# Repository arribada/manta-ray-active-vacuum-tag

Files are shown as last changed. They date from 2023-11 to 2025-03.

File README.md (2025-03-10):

# Oceanic Manta Ray Active Vacuum Tag

manta_tag

## About

This repository details ongoing research and development work by [Arribada](https://arribada.org) to develop an active vacuum (suction) cup tag, primarily to provide a non-invasive means of attaching scientific instruments to oceanic manta rays i.e accelerometers, video cameras or other instruments to advance scientific research conducted by the [Bureau of Ocean Energy Management](https://www.boem.gov/) in partnership with [Georgia Aquarium](https://www.georgiaaquarium.org/).

### Active vacuum cup "tadpole" design

manta_vacuum_tag_github

## Purpose

The oceanic manta ray active vacuum tag was developed to provide a non-invasive means of attaching bio-logging instruments to oceanic manta rays by means of utilising a vacuum cup and active suction to attach bio-logging payloads to the manta's skin. It is primarily intended for attachment in-water by scuba divers, although a pole-based attachment mechanism is under development. Typical use cases involve attaching GPS/GNSS positioning instruments, accelerometers and other bio-logging apparatus.

The tag has been designed to fit Arribada's open source [Horizon ARTIC R2 Argos satellite / GNSS transmitter](https://arribada.org/horizon-gps-tracking/) to provide satellite positioning for recovery when on the surface. Other payloads, such as accelerometers, of optional VHF pingers can be fitted to either side of the tag's cylindrical mounting holes.

The design files in this repository contain all of the components and necessary to build the physical tag. You are free to select your own electronics / payloads, or to use the Horizon transmitter which fits the tag natively.

## Design

To get started with the design, head to the [hardware](https://github.com/arribada/manta-ray-active-vacuum-tag/tree/main/Hardware) directory.
Here you will find the assembly instructions and design files for the tag.

## Changelog

### v1.02a - 2024-07-15

- Documentation clean up for public release

### v1.02 - 2024-06-01

- Initial release and publish to OSHWA

## Licence

All hardware designs, files, assets and schematics in this repository are licenced under CERN OHL v1.2. Documentation is licenced under GPLv3.
The design files are certified open source hardware by the Open Source Hardware Association, certification UID [UK000063](https://certification.oshwa.org/uk000063.html).

CERN OHL v1.2

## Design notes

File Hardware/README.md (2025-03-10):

# Hardware Design

The design specification of the payload was to primarily generate a vacuum underwater, removing water and air trapped within a vacuum cup when applied to the surface of a target animal quickly and efficiently. To achieve this, the payload itself needed to be slightly positively buoyant to aid recovery after being a) mechanically vented through the use of a corrodible plug to fill the vacuum with water and thus detach, or b) retained in place via a watertight / airtight seal until otherwise vented via a mechanical process.

Once on the surface, the tail of the tag should point towards the sky as it is the lightest part of the instrument. The base remains in the water carrying the payloads, exposing the whip antenna in the tail and allowing recovery by VHF (pinger) or Argos telemetry using an embedded [Arribada Horizon satellite transmitter](https://arribada.org/product/arribada-horizon-artic-r2-developers-kit/).

Early iterations of the design utilised a modified commerical vacuum cup insert, with an attempt to reduce total weight made by milling away surface metal of the internal disk. Ultimately the overall weight and need to include additional syntactic foam to increase buoyancy required a custom ABS insert to be CNC milled instead, replacing the metal off-the-shelf variant. An example of a typical commercial vacuum cup insert with vacuum socket has been provided below. Typically, the weight of a vacuum cup insert is not a defining factor if used in a vacuum assembly line, however in our case the weight needed to be reduced significantly.



## Manufacturing

## Version v1.02

We recommend that you inspect the [bill of materials (BOM)](./bom/manta_active_vaccum_tag_bom.xlsx) necessary to build the tag, inspect the 3D printable assets, the CNC millable assets, and all of the necessary components required to develop and test the tag before proceeding.

The tag consists of a 3D printable payload holder, typically printed in nylon (PA 11), attached to an ABS vacuum insert that are both printable and millable on suitable desktop 3D printers and mills (i.e. the Bambu X1 that supports nylon and the Carvera Desktop CNC). If you don't have access to suitable 3D printers or CNC machines the files can readily be printed and milled by third parties.

All other required components, such as the vacuum cup, air hose, venturi vacuum generator and Prevost quick attachment adapter are noted in the BOM and can be purchased from multiple online retailers.

### 1. Preparing the custom vacuum cup insert

The tag was designed to attach to and support the use of a Fipa ref.102.160.380.4 vacuum cup, a 160mm diameter cup originally designed to lift rough materials (sawn wood or materials with rough or uneven surfaces). Fipa cups can be purchased from any Fipa authorised supplier. We purchased our cups from Hennig UK Ltd, who selected the cup based on our requirements - size, grip and suitability for us to redesign a lighter open source vacuum insert to replace the metal insert that is typically used with standard vacuum machinery.

To reduce the overall weight of the tag and to increase buoyancy it was necessary to develop a custom ABS vacuum cup insert, filled with pre-cut syntactic foam, thus essentially creating a positively buoyant vacuum insert to replace the metal commerical off-the-shelf variant (described above) that was too heavy to utilise. Our re-designed insert fits the Fipa ref.102.160.380.4 vacuum cup and can be CNC milled in ABS using the supplied STEP files in the [/hardware](./cad/) directory of this repository.



When milling with a suitable CNC machine, the external (top) face of the insert needs to be milled flush (+/- 0.1mm tolerance) with a step on the lip to fit the FiPA vacuum cup (see below). In the graphic below the venting hole can be seen next to the central air extraction hole. A 1/4 BSPP non-return valve (RS PRO Non Return Valve, 10mm Tube Outlet - 144-2704) is attached after tapping the hole with a 1/4 tapping tool. Use plumbing tape (PTFE Tape) on the threads to ensure a watertight seal and secure with a 1/4 BSPP locking nut on the internal side (RS PRO Stainless Steel Locknut, 1/4 BSPP - 762-1184).



Alignment rings should be greased in a synthetic lubricant to help guide the nitrile rubber vacuum cup into position. Note - use a good amount of synthetic lubricant, such as super lube multi-purpose synthetic grease on the centre hole to help push the nitrile rubber inner ring into place. Without grease it can be quite challenging, but with grease it's possible to ease it in slowly, working your way around in a circle until the entire inner ring is flush with the ABS disk.



The FiPA nitrile rubber vacuum cup we selected is designed for stacking partially air-permeable plate materials, so we selected it to help work with the manta's slime layer that we would ultimately need to attach to. We also selected this type of cup as it has a soft sealing lip made of abrasion-resistant nitrile and has a large surface area, although we intend to replace this part for a ClingTech variant in the near future (testing is still underway) that may enhance attachment further.



### 2. Preparing the multi-jet fusion 3D printed body

The body of the tag is constructed in two halves (all STEP files are available in the hardware folder of this repo). The material used is PA 12, using either selective laser sintering (SLS) or multi-jet fusion 3D printing processes to form the body. PA 12 is porous, but as we are attaching payloads separately we don't need to worry about water ingress - instead the body forms a hydrodynamic structure in which to hold the payloads, syntactic foam and push water over the air hose coupler in the centre to minimise drag.

The image below details the assembly of the body. Accu stainless steel M4 socket flanger screws (50mm and 30mm) are used to attach the 3D printed body to the CNC milled ABS vacuum cup insert / base. Foam is cut and place in the internal cavity. Based on your choice of payload (weight), the foam can be removed or topped up as necessary to balance the tag and provide a slight amount of positive buoyancy. Mounting holes on the ABS insert are drilled to M3 in size ready to be tapped to M4 using a tapping tool. Once tapped you should drill the mounting holes out slightly in the 3D printed SLS leaving a little bite so there is additional grip still and the hole is tight to accept the screw and secure the body in place.



A complete bill of materials is available [here](./bom/manta_active_vaccum_tag_bom.xlsx) to reconstruct the tag. It should be possible to replicate the tag with access to a 3D printer, 3-axis CNC machine and a basic workbench to aid tapping the threads and installing the air hose coupler.

It's important to use a stainless steel Prevost coupler vs the standard variant as the ball-bearings inside the coupler are brass vs stainless steel and will rust over time when exposed to salt water. The image below shows a Prevost coupler attached to the tag. The green button can be pressed with a single hand when in the water to detach the coupler after air has been removed using a venturi inline in the air hose. We used an Air Engineering Controls Ltd Vacuum Pump, 19.1mm nozzle , 847mbar 3398L/min venturi connected to a standard compressed air scuba tank.



A pole attachment method using a modified bike break to depress the green button remotely is currently being design. This will enable the tag to be attached to manta rays from a boat within a few meters. Preparation of the current design has been described below.

### 3. Assembling and preparing the air system and vacuum components

The following diagram illustrates each stage of the air system, identifying the positioning of vacuum components.

manta_ray_air_system_assembly_stages

#### Stage 1 - Air tank

A standard 232 Bar scuba diving pony air cylinder can be used to provide air pressure to the system. A pony bottle is well suited as it can be carried by a diver as a separate cylinder when diving to attach the tag to the manta ray.

#### Stage 2 - Air hose from cylinder to air gun

Install a suitable air hose and tubing. Tubing length can be 1m in length as it will only need to provide adequate distance from the cylinder to the air gun held on an outstretched air of the diver. The diver will operate the air gun to provide compressed air, which will be reversed by the venturi generator creating suction to remove water from beneath the vacuum cup.

#### Stage 3 - Secure the air hose line

Install or locate a suitable position for the air gun to be attached to the diver's BCD as the diver may be in the water for some time waiting to identify a suitable manta ray to tag. A quick release mechanism is recommended, enabling the diver to move freely in the water without the hose dragging.

#### Stage 4 - Tighten and maintain valves

Before tagging, test that your valves are clean and adequately tight as a loss of pressure can affect the speed in which the tag can attached if the venturi is supplied with less pressure that is it expecting.

#### Stage 5 - Air gun

A standard air gun nozzle / convertor for scuba tanks works well to provide the compressed air source. [This is the air gun](https://www.diversdirect.com/p/quick-release-metal-air-blower-gun) utilised during our tests.

#### Stage 6 - Air hose valve and venturi valve

Select a suitable valve to connect to your air gun's outlet that allows you to fit 8mm OD (outer diameter) and 6mm (inner diameter) tubing, as the tubing will need to fit a G1/8 threaded valve on the venturi

#### Stage 7 - Air hose to venturi

The air hose should have a G1/8 valve fitted to mate with the air supply in (E) threaded valve socket on the venturi.



#### Stage 8 - Valve maintenance, air in

Salt will collect in the valves of the venturi vacuum and will ultimately reduce pressure. Ensure tubes and the venturi's valves are cleaned after deployment in saltwater.

#### Stage 9 - Venturi (Vacuum generator)

Connect the air hose from the air gun to valve E (G1/8) and connect another hose from the vacuum port J (G1/4) using the 10mm ID, 12mm OD tubing. The venturi will create a vacuum and remove air / liquid through the exhaust when over 3.5 bar of pressure from a compressed air source is applied. You can test that your venturi is working by applying compressed air and observing the tag sink down on a flat surface (i.e. a table) as air is removed from under the vacuum cup. In water you will see air bubbles escaping from the exhaust. The black exhaust port is a silencer used with air and can be removed if used in water as it does not function in the same way when used with liquids.

#### Stage 10 - Valve maintenance, water out

Salt will collect in the valves of the venturi vacuum and will ultimately reduce pressure. Ensure tubes and the venturi's valves are cleaned after deployment in saltwater.

#### Stage 11 - Step down adapter

The prevost quick release S1 adapter requires 8mm tubing, so a reducer nipple is required to step down the 12mm tubing (OD) from the venturi G1/4 valve socket. Connect the reducer nipple inline using the Festo adapter.

#### Stage 12 - Connect tubing to the Prevost S1 quick release coupler

Connect the tubing to the adapter on the Prevost S1 and then connect the S1 to the tag's quick release adapter. You have now completed assembling the air system. By pressing the quick release button on the Prevost S1 the adapter will release the coupler and detach the tag. Pushing the Prevost back onto the tag's connector will re-attach the air system to the tag.

### Step 4. Preparing and installing the buoyancy aid (closed cell foam)

As noted in Step 1, the use of syntactic foam is necessary to generate the buoyancy required for the tag to float when dislodged from the manta for recovery. The tail of the tag lifts the tip up when on the water's surface, pointing any antennas you attach (i.e. Argos satellite antenna) towards the sky. The heavier vacuum disk and Prevost S1 coupler point down. Syntactic form should be added to the cavity of the tag's body and a thin layer applied inside the vacuum disk insert (see Step 1) to reduce overall weight. The cutting guide below identifies the dimensions of the foam required to cut and fill the cavity. It is recommended to print a template file using a 3D printer and cut / sandpaper Subsea Buoyancy Foam (R-3318) to fill the cavity.

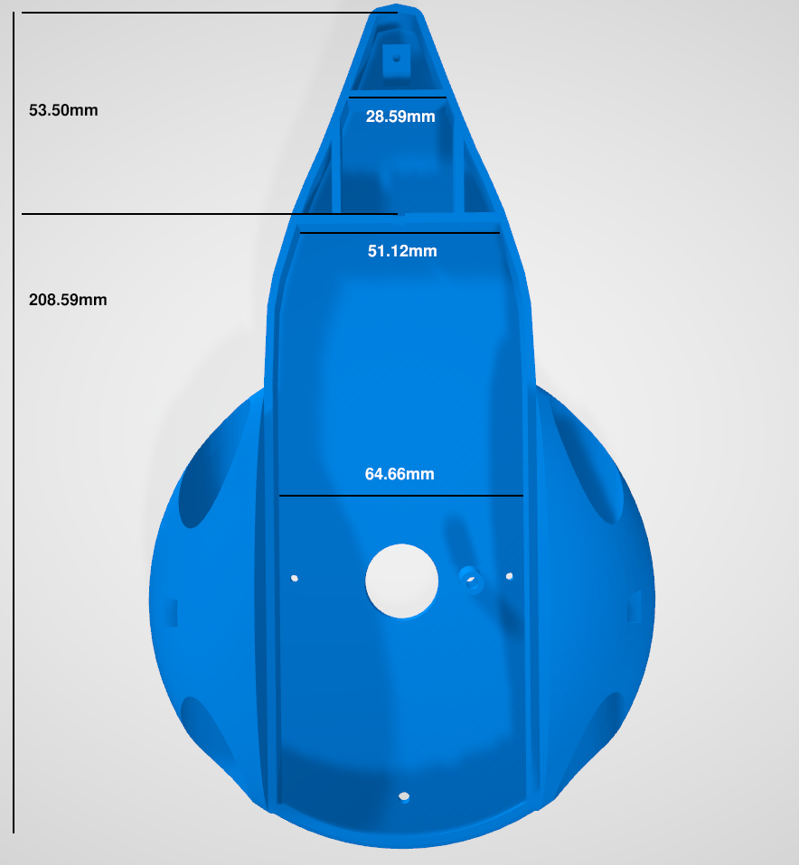
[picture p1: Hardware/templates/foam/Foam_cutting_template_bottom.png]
Foam_cutting_template_bottom


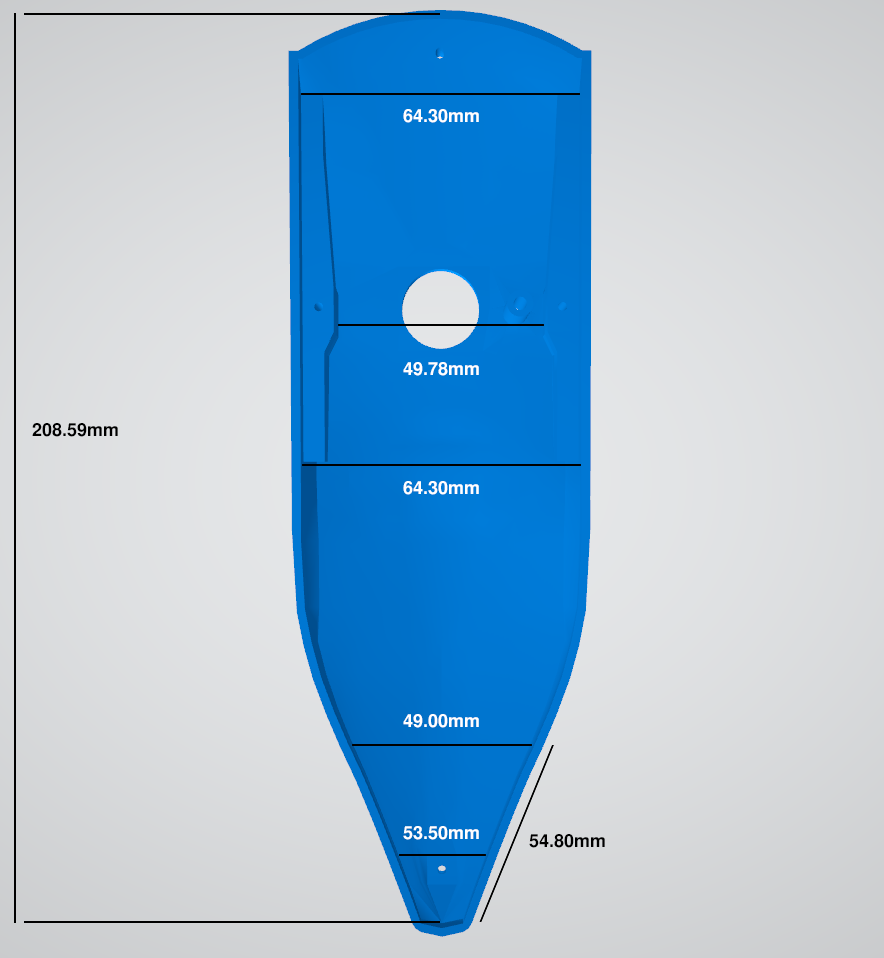
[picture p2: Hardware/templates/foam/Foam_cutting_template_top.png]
Foam_cutting_template_top


### Optional pole release mechanism

## Step 5. (Experimental) Preparing the multi-jet fusion 3D printed pole mount head

An optional 3D printed pole mount that fits the provost is available to trial. Print the pole head mount (see BOM) using MJF as the process and PA 11 as the material. PA 12 should also be suitable. Once printed, use a tapping kit to manually tag the top hole using an M9 x 1.25 tapping bit. Next, insert a 1/4" female screw adapter into the socket using pliers.



A stainless steel 360 degree swivel camera mount adapter can then be attached to the pole mount head and to a suitable telescopic boom pole that has a 1/4" thread embedded, such as the range of fibreglass poles from compositepoles.co.uk.

To fit and seat the bicycle brakes, first slot the Prevost S1 coupler into the pole head slot. Use the grip indents to guide it into place. Then slow the two M8 x 60mm socket flanged button screws through the bottom holes and secure the brakes in place using 4 x M8 hexagon nuts to align the brake in place.

## Continued research

We are continuing to explore the material properties of the nitrile rubber in comparison to other vacuum cup materials, notably ClingTech vacuum cups that we believe may enhance the longevity of attachments. To date this tag design has achieved a 4 hour attachment, with a goal to exceed 24 hours as the design is further enhanced. An internal Arribada Horizon Argos ARTIC R2 transmitter can also be loaded into the tag to enable recovery of the tag in the open ocean using Argos satellite telemetry (doppler).

Once completed and tested, the final pole attachment design will be uploaded to this repo to aid attachment.

### Pole attachment design

manta_ray_pole_102_jpeg

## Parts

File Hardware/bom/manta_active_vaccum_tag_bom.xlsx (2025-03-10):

Designator | Component | Number | Cost per unit -currency | Total cost - | Source of materials | Material type
 |  |  |  | currency
BT1 | Body top | 1 | $104.76 | $104.76 | Protolabs (https://protolabs.com/) | SLS PA 12 smooth white 3D print
BB1 | Body bottom | 1 | $69.19 | $69.19 | Protolabs (https://protolabs.com/) | SLS PA 12 smooth white 3D print
VCI1 | Vacuum Cup Insert | 1 | $266.73 | $266.73 | Protolabs (https://protolabs.com/) | ABS Black
BA1 | Body assembly | 1 | $3.10 | $3.10 | Accu (https://www.accu.co.uk/flanged-button-screws/376812-SSBF-M3-20-A4) | Accu Marine M3x20mm socket flanged bolts
BA2 | Body assembly | 1 | $3.10 | $3.10 | Accu (https://www.accu.co.uk/flanged-button-screws/376815-SSBF-M3-30-A4) | Accu Marine M3x30mm socket flanged bolts
BA3 | Body assembly | 1 | $3.10 | $3.10 | Accu (https://www.accu.co.uk/flanged-button-screws/376819-SSBF-M3-50-A4) | Accu Marine M3x30mm socket flanged bolts
VC1 | Vacuum cup | 1 | $73.91 | $73.91 | Vacuum Cups UK (https://www.vacuumcups.co.uk/) | Fipa ref.102.160.380.4
PC1 | Prevost coupler | 1 | $69.44 | $69.44 | Rowse Pneumatics (https://www.rowse-pneumatics.co.uk/prevost-esi-071808he) | ESI-071808HE 8mmID HOSETAIL COUPLING PREVOST STAINLESS STEEL
PA1 | Prevost adapter | 1 | $1.80 | $1.80 | Indanc (https://www.indanc.com/Catalogue/Compressed-Air/Quick-Release-Couplings/Prevost-Quick-Release-Couplings/Prevost-ESI-Coupling-Range/Prevost-ERP-07-Tapered-Male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) | 1/4 BSPT MALE ADAPTOR PREVOST S1
LN1 | Lock Nut | 1 | $3.09 | $3.09 | RS Components (https://uk.rs-online.com/web/p/sensor-accessories/7621184?gb=s) | RS PRO Stainless Steel Locknut, 1/4 BSPP - 762-1184
NRV1 | Non return valve | 1 | $7.38 | $7.38 | RS Components (https://uk.rs-online.com/web/p/pneumatic-non-return-valves/1442704?gb=s) | RS PRO Non Return Valve, 10mm Tube Outlet - 144-2704
VC1 | Venturi connection | 2 | $19.22 | $38.44 | RS Components (https://uk.rs-online.com/web/p/hose-pipe-flexible-tubes/2732539?gb=s) | RS PRO Silicone, Flexible Tubing, 6mm ID, 8mm OD, Translucent, 2m
RN1 | Reducer Nipple | 1 | $12.40 | $12.40 | RS Components (https://uk.farnell.com/festo/qs-12-8/push-in-fitting-12mm-21mm/dp/3431817?cjdata=MXxZfDB8WXww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) | Festo QS Series Reducer Nipple, Push In 12 mm to Push In 8 mm, Tube-to-Tube Connection Style, 130608
PH1 | Prevost hose | 2 | $19.22 | $38.44 | RS Components (https://uk.rs-online.com/web/p/hose-pipe-flexible-tubes/2732495) | RS PRO Silicone, Flexible Tubing, 10mm ID, 12mm OD, Translucent, 2m
VVG1 | Venturi vacuum generator | 1 | $215.58 | $215.58 | RS Components (https://uk.rs-online.com/web/p/vacuum-generators/8415160) | Air Engineering Controls Ltd Vacuum Pump, 19.1mm nozzle , 847mbar 3398L/min, S80 series
BA1 | Buoyancy aid | 1 | $223.20 | $223.20 | Blue Robotics (https://bluerobotics.com/store/watertight-enclosures/buoyancy/float-r3318-r1/) | Blue Robotics LAST-A-FOAM® R-3318

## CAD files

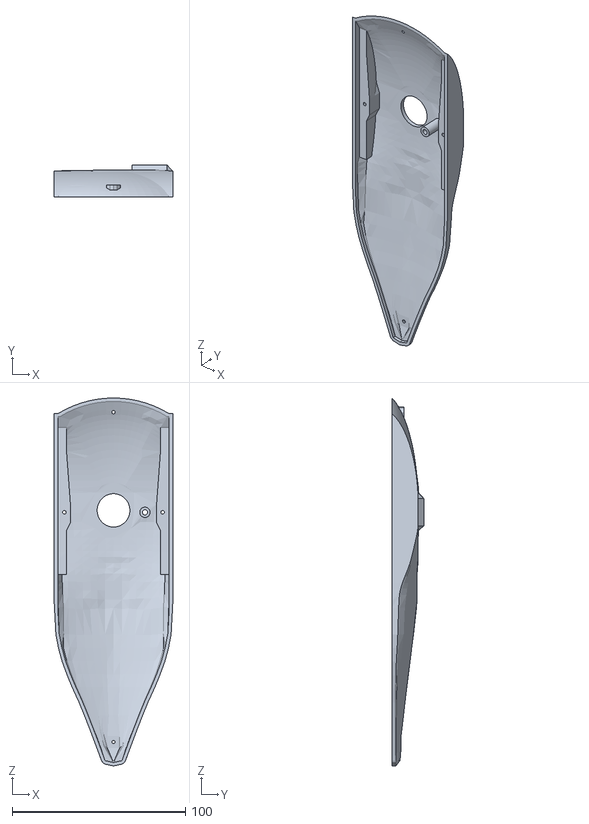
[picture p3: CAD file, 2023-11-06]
Hardware/CAD/MantaCase_Tadpole_20221208_Top.obj
68.6 x 18.5 x 212.7

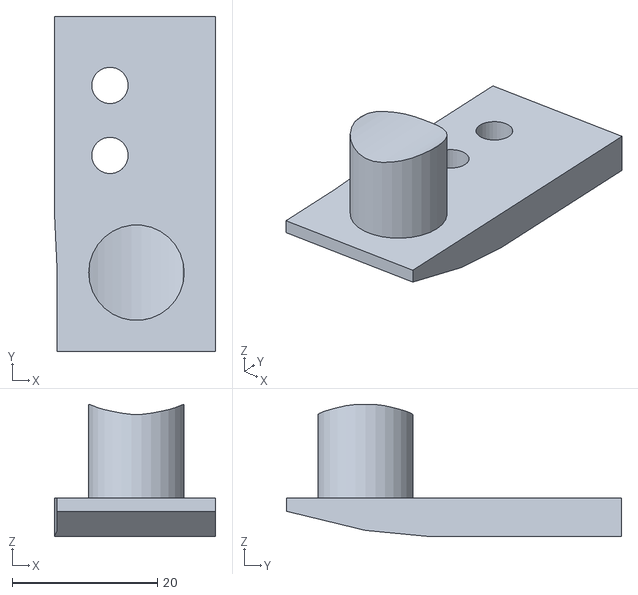
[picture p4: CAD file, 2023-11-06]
Hardware/CAD/GrabberReleaseSystem_Mk002_PusherDev002.stl
22.2 x 46.1 x 18.2

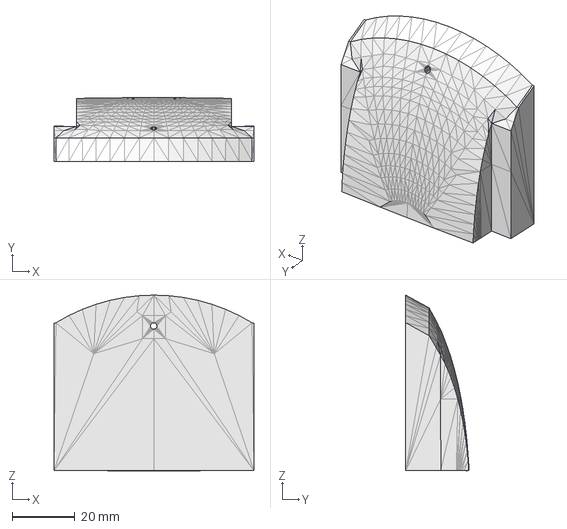
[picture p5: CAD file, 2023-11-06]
Hardware/CAD/InternalMantaResinCase_20221208.step
63.5 x 20.2 x 55.8 mm

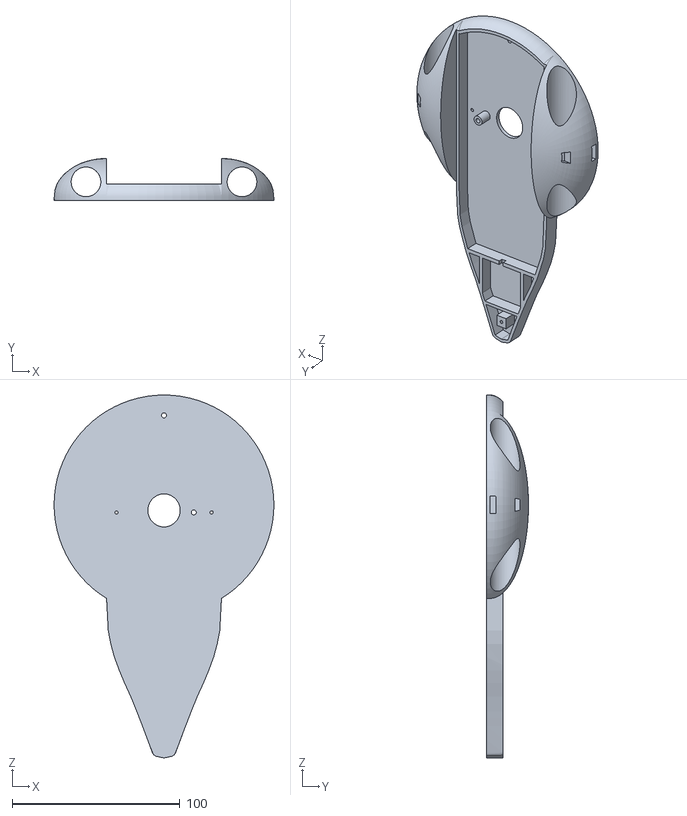
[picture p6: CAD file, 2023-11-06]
Hardware/CAD/MantaCase_Tadpole_20221208_Bottom.obj
131.3 x 25.1 x 216.7

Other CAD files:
Hardware/CAD/InternalMantaResinCase_20221208.obj

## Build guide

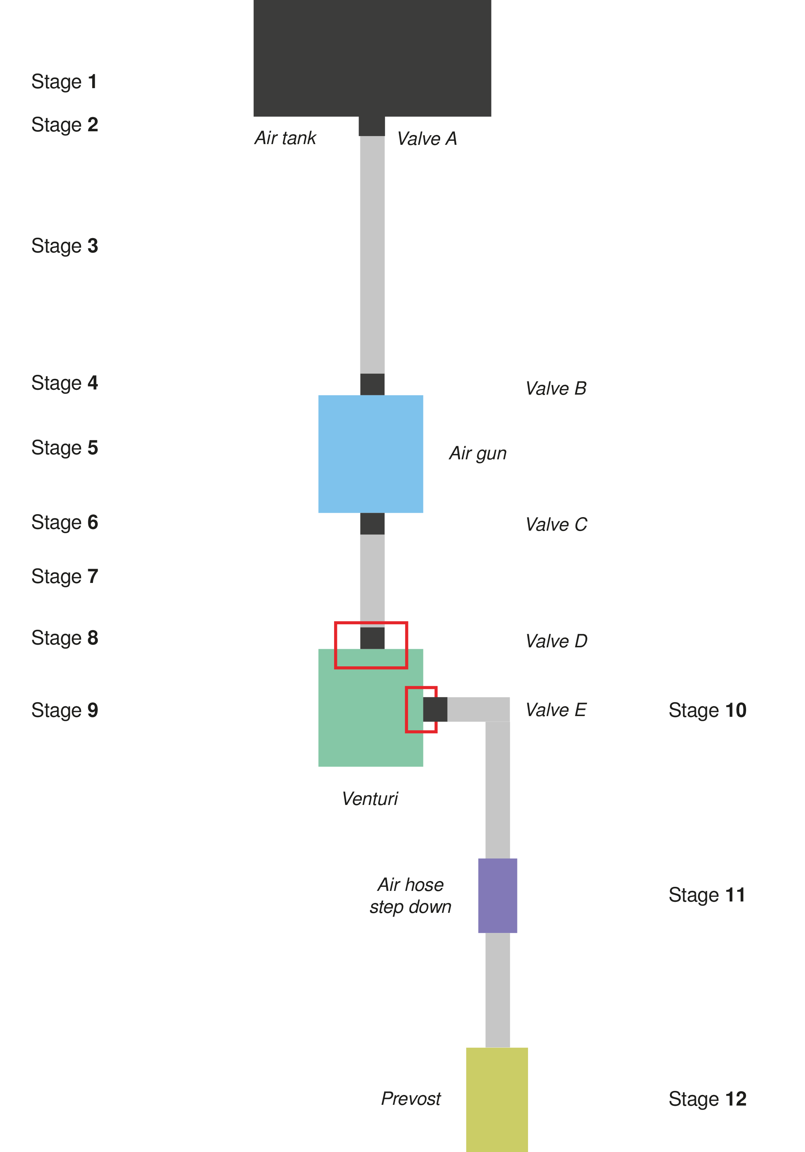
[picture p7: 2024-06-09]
Hardware/assembly/manta_ray_air_system_assembly_stages.png

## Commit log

2023-11-06 Update README.md
    Included new images and an assembly photograph.
2023-11-06 Uploaded bill of materials
    Included the BOM list and other assets
    [GrabberReleaseSystem_Mk002_PusherDev002.stl, InternalMantaResinCase_20221208.obj, InternalMantaResinCase_20221208.step, Manta active vaccum tag BOM.xlsx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]
2023-11-06 Updated BOM
    [Manta active vaccum tag BOM.xlsx]
2024-01-15 Update README.md
    Updated from M3 to M4 (screw size error)
2024-01-16 BOM update
    Updated BOM
    [Manta active vaccum tag BOM.xlsx]
2024-04-24 BOM update
    Updating the BOM with airline tubing diameters
    [Manta active vaccum tag BOM.xlsx]
2024-06-09 Updated assets
    Included additional assembly steps
    [GrabberReleaseSystem_Mk002_PusherDev002.stl, InternalMantaResinCase_20221208.obj, InternalMantaResinCase_20221208.step, Manta active vaccum tag BOM.xlsx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]
2024-06-09 Updated README.md
    Included additional assembly stages.
2024-06-09 Updated README.md
    Included additional assembly steps.
2024-06-09 Updated various assets
    [Manta active vaccum tag BOM.xlsx]
2024-07-15 Updates documentation for public consumption
    Change-type: minor
    [manta_active_vaccum_tag_bom.xlsx]
2025-03-10 Update Manta active vaccum tag BOM.xlsx
    Updated the BOM
    [Manta active vaccum tag BOM.xlsx]
